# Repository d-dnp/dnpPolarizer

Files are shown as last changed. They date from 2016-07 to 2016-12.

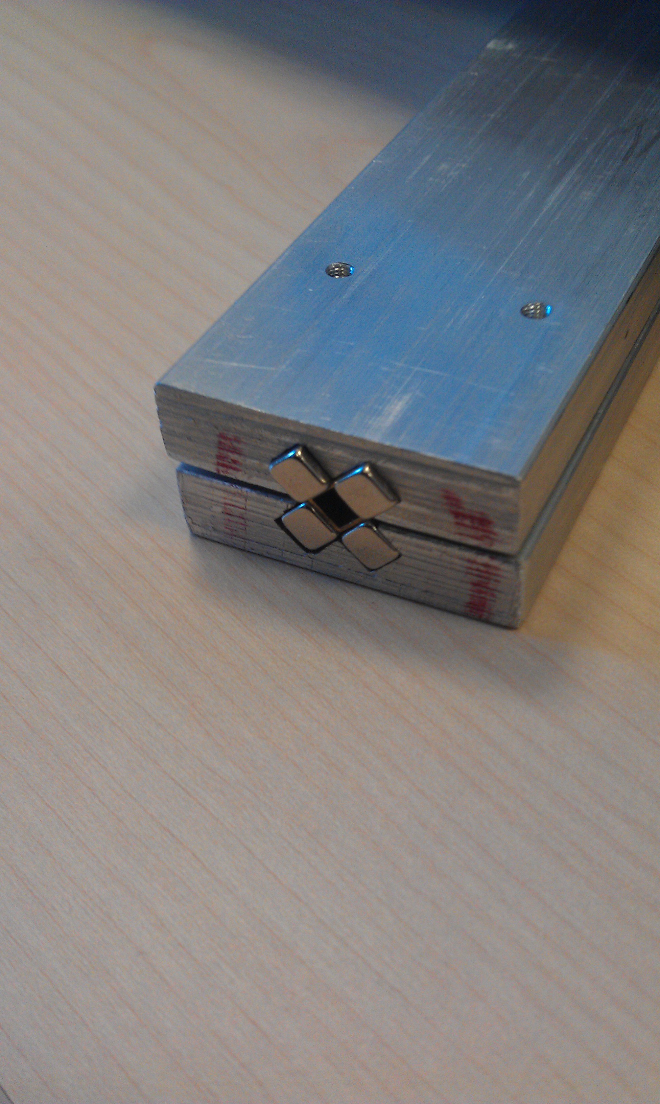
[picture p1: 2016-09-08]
magneticTunnel/Photos/IMAG0099.jpg

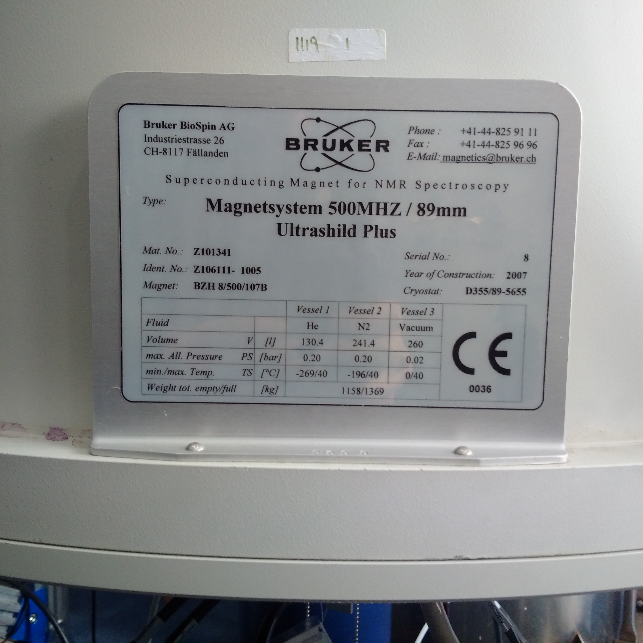
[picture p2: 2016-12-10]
magnet500/magnetInfoPlate500.jpg

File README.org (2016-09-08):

#+TITLE: Dissolution-DNP Polarizer at Southampton University

* Project description
Dissolution-Dynamic Nuclear Polarization (d-DNP) is a technique to enhance the nuclear magnetic reosonance (NMR) signal of small molecules / metabolites by several orders of magnitude. 

Clinical and pre-clinical systems are available commercially, but are costly and cannot provide the felixibility to implement new experimental procedures.

This repository contains the design of the dissolution-DNP system at Southampton University. We hope that it will become a valuable ressource for people working in the field and would be grateful for external contributions / modifications.

Using Trityl and pyruvic acid, a polarization level of 18 % was achieved.

Using TEMPOL and H2O/d-glycerol, a polarization level of 12 % was achieved on sodium acetate.

* The setup at Southampton

The system operates at 6.7 Tesla and uses an Oxford Instruments Spectrostat flow cryostat and a roots pump.

The key components that we are using are as follows: 
| Component                 | Manufacturer       | Approximate Price (EURO)            |
|---------------------------+--------------------+-------------------------------------|
| 6.7 Tesla SWB Magnet      | Bruker             | 60 k (used WB magnets are suitable) |
| Spectrostat Flow Cryostat | Oxford Instruments | 20 k                                |
| Roots Pump, RUVAC WAU251  | Oerlikon           | 20 k                                |
| 188 GHz Microwave Source  | ELVA               | 20 k                                |
| Mini NMR Spectrometer     | Magritek           | 20 k                                |

The use of the Spectrostat Flow cryostat currently limits the temperature to above 2.1 K in continuous mode and 1.8 K in single-shot mode (hold-time approximately 45 mins). 

Options for cryostats with lower base temperature are currently being explored.

** Custom-built components

In addition to these componets, we have designed and built various pieces of instrumentation, listed below. We will shortly add a README file to each of the corresponding folders to provide further information. The mechanical design was performed in SolidWorks. The control electronics rely on the Arduino platform, for which custom printed-circuit board (PCB) extensions, referred to as shields, have been designed in Eagle. The radio-frequency design has been simulated in Python. The project is documented using Emacs org-mode. 

*** DNP insert and CryoShield
The dnp insert allows to irradiate the sample with microwaves at low temperatures down to 1.6K and measure its polarization by NMR. It also hosts a set of Allen-Bradley resistors attached to a custom-built controller/shield. This shield applies 5V pulses to the resistors and measures their resistance as function of time immediately after the pulse. Currently our insert is equipped with coils for 13C and 1H. The coils are roughly tuned and matched with ATC700B chip capacitors, fine tuning is done at room temperatures using an L-Network of Jennings capacitors 1.5 - 45 pF, and optionally coaxial line stretchers (trombone lines) by Microlab.

*** Dissolution Wand and Controller
The controller for the dissolution wand comprises a 220 V to 110 V transformer, whose output can be connected to a mineral barrel heater on the dissolution wand. It also hosts a custom shield that measures the temperature and pressure within the dissolution wand via simple voltage dividers. Finally the controller hosts a relay board to control the various (pilot) valves in the system, including those that drive the dissolution. 

*** Magnetic Tunnel
Following dissolution the solute is flushed to our 500 MHz liquid-state NMR magnet via a magnetic tunnel to reduce low-field relaxation. 

*** Injector
An injector has been designed to fit into our 500 MHz magnet. 

*** Arbitrary Waveform Generator
An arbitrary waveform generator providing an output of up to 24 V has been designed to allow sweeps of the microwave source. We are not using it routinely at the moment, though it is fully functional. 
This device is based on an Arduino Due.

* Procedures
** Sample preparation
More detailed procedures will be in the sample preparation folder.

** Probe tuning
We use an Agilent FieldFox Network Analyser to tune and match our probes. More details will be published soon.

* Acknowledgement
We would like to thank Sami Jannin, Jonas Milani, Jan Hendrik Ardenkjaer-Larsen, Arnaud Comment and Jacques van der Klink for discussions and advice.

* License
#+BEGIN_HTML
<a rel="license" href="http://creativecommons.org/licenses/by-sa/3.0/"><img alt="Creative Commons License" style="border-width:0" src="https://i.creativecommons.org/l/by-sa/3.0/88x31.png" /></a><br />This work is licensed under a <a rel="license" href="http://creativecommons.org/licenses/by-sa/3.0/">Creative Commons Attribution-ShareAlike 3.0 Unported License</a>.
#+END_HTML

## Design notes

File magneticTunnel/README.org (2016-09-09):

* Magnetic Tunnel

** Why 
 
Dissolution-dynamic nuclear polarization (D-DNP) experiments require the use of radical which, when the sample is shuttle through a region of low magnetic field a detection magnet, are efficient in driving longitudinal relaxation of the hyperpolarized substance of interest. A magnetic tunnel has therefor been constructed to provide a high magnetic field region between polarizer and detection magnet to minimise the effect of longitudinal relaxation from dissolved radicals.

** Specs 

Permanent magnets are 5 mm x 5 mm x 50 mm in size and were magnetised to 1x10^6 Am^2 through the short axis. A Haibach array was constructed by arranging permanent magnets in a square with alternating polarity as to augment the magnetic field in the centre of the array creating a magnetic field strength of 0.74 T along the majority of the magnetic tunnels is 2.1 m length. Two magnets, from opposite faces, are removed at each end of the tunnel to avoid flipping the direction of the location magnetic field and ensure a smooth, adiabatic transition from polarizer to magnetic tunnel to detection magnet.

** Results

The magnetic tunnel is predicted to save ~14% spin polarization throughout the dissolution process. Enhancement figures for carbon-13 in sodium acetate without the magnetic tunnel is ~1,500 and with the magnetic tunnel is ~3,900.

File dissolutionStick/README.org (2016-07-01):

#+Title: Dissolution Stick + Box Documentation
This document contains documentation on the wiring / part nos. for the dissolution stick and its controller box.

The controller also drives the pilot valves via 24V lines. A relay module is driven by the Arduino's digital outputs and connects the 24V output of the power supply to the various pins of a DB25 connector on the front panel. 
* Content

** Dissolution Stick
*** Parts
| Part                           |   Order Code | Company  |
|--------------------------------+--------------+----------+
| Pressure Transducer            |     457-3170 | RS       |
| Pt-100                         |     237-1607 | RS       |
| LED green                      |     234-9458 | RS       |
| LED red                        |     234-9420 | RS       |
| Push button with LED           |     729-5429 | RS       |
| Aluminium plates               |      187-328 | RS       |
| M3 Hex Screws                  |     660-4636 | RS       |
| Fischer Connector on Cable     |     726-3337 | RS       |
| Fischer Connector Sleeve       |     1031.855 | RS       |
| Cable: Farnell                 |     119-0173 | Farnelll |
| Manual Valve                   |      SS-4P4T | Swagelok |
| Activated Valve                | 6LVV-DPS6M-C | Swagelok |
| 1/8" Replacement Front Ferrule |      A-203-1 | Swagelok |
| 1/8" Replacement Back Ferrule  |      A-204-1 | Swagelok |
| 1/8" Nylon Nut                 |     NY-202-1 | Swagelok |
| Union cross                    |              | Swagelok |
| Port Connector                 |              | Swagelok |

*** Wiring / Info

** Dissolution Box Controller
*** Dissolution Control
**** Parts
| Part                        | Order Code | Company            |
|-----------------------------+------------+--------------------|
| Rack case 3U                |   665-7637 | RS                 |
| Rack case vented cover      |   665-7652 | RS                 |
| TXL Universal Power Supply  |   418-2308 | RS                 |
| Power switch, fused 4A      |   456-0988 | RS                 |
| Arduino Mega                |            |                    |
| Arduino Ethernet            |   769-7415 | RS                 |
| (Mounting Plate)            |   349-7895 |                    |
|                             |            |                    |
| RJ45 Connector              |   706-0194 | RS                 |
| 5V Solid State Relay module |            | SainSmart / Amazon |
| Transformer Toroidal        |   223-8128 | RS                 |
**** Rack Parts
| Castors for universal rack |   433-7299 |   62.25 |
| 6 way power block          |   686-6165 |  34.704 |
|----------------------------+------------+---------|

**** Wiring / Info
Use C-u <TAB> to expand content
| Colour | Terminal 1         | Terminal 2            | Pin No. on Fischer Connector |
|        |                    |                       |   <5> |
|--------+--------------------+-----------------------+-------|
| Blue   | GND                | GND                   |     1 |
| Green  | 110V AC            | Mineral band heater   |     2 |
| Red    | 110V AC            | Mineral band heater   |     3 |
| Grey   | to GND via A2,100R | Pressure Transducer - |     4 |
| Yellow | EARTH              | EARTH                 |     5 |
| White  | +24V               | Pressure Transducer + |     6 |
| Black  | EARTH              | EARTH                 |     7 |
| Brown  | to 5V via A1,470R  | PT100                 |     8 |
| Violet | to 5V via A0,2K2   | Push button           |     9 |
| Orange | to PIN 10 via 470R | Push button LED       |    10 |
| Rose   | to PIN 11 via 470R | Red LED               |    11 |
| Cyan   | to PIN 12 via 470R | Green LED             |    12 |
| -      | PIN 13             | TTL In, 10K to GND    |       |
| -      | PIN A4             | TTL OUTB              |       |
| -      | PIN A5             | TTL OUTA              |       |

*** Valve Control
**** Parts 
| Part                        | Order Code | Company            |
|-----------------------------+------------+--------------------|
| Sain Smart 5V Relais Module |            | SainSmart / Amazon |
|                             |            |                    |
**** Wiring / Info

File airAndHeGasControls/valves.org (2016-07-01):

* Swagelok actuators
http://www.swagelok.com/downloads/WebCatalogs/EN/MS-02-343.pdf

* Swagelok pneumatically actuated 2 way ball-valve
[[http://www.swagelok.com/search/find_products_home.aspx?part=SS-42GS4-31C#][SS-42GS4-31C]]
243.65 GBP

* Adapter Actuator to 6 mm tubing: RS 536-2606 

* SMC Manifold
** Manifold
http://uk.rs-online.com/web/p/products/762-2036/?origin=PSF_428500|QVBasket%20Summary-LL
222.28 GBP
762-2036
SMC 
SS5Y3-10F1-12B-C6

** Blanking plate
http://uk.rs-online.com/web/p/blanking-plates-for-pneumatic-control-valves/7622095/?origin=PSF_428499|acc
5.14 GBP
762-2095

* SMC Valve
SY3A00-5U1
http://uk.rs-online.com/web/p/pneumatic-solenoid-pilot-operated-control-valves/7622076/
70.83 GBP
762
* Silencer
http://uk.rs-online.com/web/p/pneumatic-silencer-exhaust-restrictor-function-fittings/7622082/
3.43 GBP
762-2082

* 6 mm feed-through
Bulkhead Union 6mm
http://uk.rs-online.com/web/p/pneumatic-bulkhead-tube-to-tube-adaptors/7714936/
4.27 GBP (5 MOQ)
SMC 
KQ2E06-00A

* MOSFET DRIVER 24V
ZXGD3003E6TA, MOSFET Power Driver 5A, Non-Inverting, Maximum of 40V, 6-Pin SOT-23
http://uk.rs-online.com/web/p/mosfet-power-drivers/7122839/
0.189 GBP (50 OQ)

* 25 pin d-sub pcb
http://uk.rs-online.com/web/p/pcb-d-sub-connectors/7183474/

* Feed through for dissolution stick
** Plug (max cable diameter 6.7mm, 0.79mm)
http://uk.rs-online.com/web/p/industrial-automation-circular-connectors/7263324/
PLUG, IP68, PUSH-PULL, 7WAY
33.30 GBP

** Receptable
http://uk.rs-online.com/web/p/industrial-automation-circular-connectors/7263390/?origin=PSF_435588|acc
726-3390
38.58 GBP

* Cable
http://uk.rs-online.com/web/p/cy-cable/4451682/
445-1682
118.02

* Drill/Driver
http://uk.rs-online.com/web/p/cordless-drills-drill-drivers/7525424/
18V XR Li-Ion Compact Drill Driver
215 GBP

* SETUP
  PinOut: [[./SY3000-5000_B_EU-1.pdf::36][Manual page 57]]
  In any case common is pin 13pn
  Pin 1 is the row with more pins, on the side opposite to the
  ports. Then it is clockwise. 

  Next check, if the valve has polarity. Our valve is SY3A00-5U1. U is
  unpolar, so this should be fine. So we have
| Station | Pin | Farbe  |
|---------+-----+--------|
|       1 |   1 | weiss  |
|       2 |  14 | grau   |
|       3 |   2 | lila   |
|       4 |  15 | blau   |
|       5 |   3 | gruen  |
|       6 |  16 | gelb   |
|       7 |   4 | orange |
|       8 |  17 | rot    |
|       9 |   5 |        |
|      10 |  18 |        |
|      11 |   6 |        |
|      12 |  19 |        |

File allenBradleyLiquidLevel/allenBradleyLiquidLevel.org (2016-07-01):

* Configuration.

We use three AB sensors with 100 Ohm resistance at room temperature. They are wired with a 0.2  mm diameter copper cable.

The pin numbering is as follows (the first 4 pins drive current through the resistors.

| Pin | What                           | Color in Cable Assembly |
|-----+--------------------------------+-------------------------|
|   1 | Top AB high side               |                         |
|   2 | Top AB low / Centre AB high    |                         |
|   3 | Centre AB low / Bottom AB high |                         |
|   4 | Bottm AB low                   |                         |
|   5 | AD Top + (parallel to wire 1)  |                         |
|   6 | AD TOP -                       |                         |
|   7 | AD centre +                    |                         |
|   8 | AD centre -                    | red-black               |
|   9 | AD bottom +                    | green-black             |
|  10 | AD bottom -                    | orange-black            |
|  12 | NC                             | blue-black              |
|  14 | Cernox current +               |                         |
|  15 | Cernox current -               |                         |
|  16 | Cernox AD+                     |                         |
|  17 | Cernox AD-                     |                         |

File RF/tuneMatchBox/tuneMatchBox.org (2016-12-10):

* Materials
** Jennings Capacitors
2 x CHV1N-45-0105, 1.5 - 4.5 pF
[[./datasheets/45-260pF-Variable-and-Fix-Vacuum.pdf]]

*** Thread at Shaft: 3/8 32 UNEF
Order code for nut at Farnell: 1202035 

*** Thread at Top: 
1/4 28 UNF Tap: RS: 241-5117
Also fits 1/4 28 fitting for PTFE tubing

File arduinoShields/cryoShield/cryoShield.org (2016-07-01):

This document contains info regarding the wiring of the cryoShield as defined in the eagle [[./cryoShield.brd][file]].

The documentation of the corresponding breakout box can be found here [[/Users/benno/Dropbox/RESEARCH/newPolarizer/cryostats/breakoutBoxOle/breakoutBoxOle.org][here]]

ADG3331 selects the driving potential / current source. 
ADG3332 wires the return path.

See the [[./ADG333A.pdf][manual]].

For Logic 1 Input, Switches switch to the A output

The CS for the AD 7794 was pin 10.

Note that this sketch requires Arduino Pin 4 high to connect the drive current to PIN 1. At the same time Arduino Pin 4 is the Chip Select for the SD functionality.

* BOM 
| Part            | RS Order Code | Quantity |
|-----------------+---------------+----------|
| ADP3303ARZ-3.3  |      697-7713 |        1 |
| Cap 0.1 uF 0805 |      264-4416 |        5 |
| Cap 10 uF 1206  |      464-9069 |        1 |
| Res 220k 0805   |      804-6625 |        1 |
| USB B to USB A  |      815-8466 |        1 |
| AD7794CRUZ      |      709-6676 |        1 |
|                 |               |          |

* Pins
| Arduino Pin | Functionality | Secondary Device | HIGH Connect to | Low Connect to  |
|-------------+---------------+------------------+-----------------+-----------------|
|           0 | free          |                  |                 |                 |
|           1 | free          |                  |                 |                 |
|           2 | IN11          | ADG3331          | +5V             | AD7794 I1       |
|           3 | IN12          | ADG3331          | ADG3331 D3      | ADG3331 D4      |
|           4 | IN13, CS SD   | ADG3331          | Pin 1           | Pin 2           |
|           5 | IN14          | ADG3331          | --              | Pin 3           |
|           6 | IN21          | ADG3332          | 470 Ohm to GND  | GND             |
|           7 | IN22          | ADG3332          | ADG332 D3 to D1 | ADG332 D4 to D1 |
|           8 | IN23          | ADG3332          | Pin 2           | Pin 3           |
|           9 | IN24          | ADG3332          | --              | Pin 4           |
|          10 | CS ETHERNET   |                  |                 |                 |

* Pin Configurations Drive Path
| 2 | 3 | 4 | 5 | Function              |
|---+---+---+---+-----------------------|
| 0 | 0 | 0 | 0 | Connect I1 to Pin 3   |
| 1 | 0 | 0 | 0 | Connect +5V to Pin 3  |
| 1 | 1 | 0 | 0 | Connect +5V to Pin 2  |
| 1 | 1 | 1 | 0 | Connnect +5V to Pin 1 |

* Pin Configuration Return Path
| 6 | 7 | 8 | 9 | Function              |
|---+---+---+---+-----------------------|
| 0 | 0 | 0 | 0 | D1 to GND             |
| 1 | 0 | 0 | 0 | D1 to 470 Ohm to GND  |
| 0 | 0 | 0 | 0 | D4 to D1, Pin 4 to D1 |
| 0 | 1 | 0 | 0 | D3 to D1, Pin 3 to D3 |
| 0 | 1 | 1 | 0 | D3 to D1, Pin 2 to D1 | 

* Probing conditions
Hence for probing the first, second and third resistor with I1, the following pin configurations apply.

Note, that if you want to chase +5V to drive, just set Pin 2 HIGH

The return path connects straight to GND. If you want to connect via 470 Ohm to GND, just set Pin 6 HIGH.

Pin 5 is always low, it connects to Pin 3 and there is no 4th drive pin.
Likewise, Pin 9 is always low, it connects the return path to Pin 4. 

| 2 | 3 | 4 | 5 | 6 | 7 | 8 | 9 | Functionality                             |
|---+---+---+---+---+---+---+---+-------------------------------------------|
| 0 | 1 | 1 | 0 | 0 | 1 | 1 | 0 | Connect I1 to Pin 1, Return Path to Pin 2 |
| 0 | 1 | 0 | 0 | 0 | 1 | 0 | 0 | Connect I1 to Pin 2, Return Path to Pin 3 |
| 0 | 0 | 0 | 0 | 0 | 0 | 0 | 0 | Connect I1 to Pin 3, Return Path to Pin 4 |

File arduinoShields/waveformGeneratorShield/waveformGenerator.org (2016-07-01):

* Description
A waveform generator to sweep microwave frequencies.

It is build around the Arduino Due, DAC0 is used to set the offset,  and DAC1 is used to generate the periodic waveform.

A summing OP amp (AD823, supplied with +/-15 V) is used to generate - (3*V_DAC0 + DAC1). 
The signal is then inverted (AD823).
Then it is fed into a gain = 2 non-inverting Amplifier (again AD823, but powered with +24V / GND. 

At last the signal is filtered by a third order  Butterworth filter with a cutoff frequency of 100 kHz.

* Parts
| Description                       | Brand           | RS order code |
|-----------------------------------+-----------------+---------------|
| TMP15215C Power supply            | Traco           |       6641474 |
| TMP15124C Power supply            | Traco           |       6641468 |
| TMP15105C Power supply            | Traco           |       6641461 |
|-----------------------------------+-----------------+---------------|
| Interscale M19" Enclosure 2U      | Schroff         |       8104387 |
| Mounting plate                    | Schroff         |       8104425 |
| PCB holder                        | Schroff         |       8104529 |
| LED 12V                           | RS Pro          |       8987683 |
| Ethernet Connector                | TE Connectivity |       7060194 |
| USB Connector                     | Harting         |       7658757 |
| BNC Connector                     | TE Connectivity |       5121174 |
| OR SMA Connector                  | TE Connectivity |      512-0008 |
| Mains connector                   | Bulgin          |      211-0985 |
| Slow blow Fuse                    | Schurter        |       7897801 |
|-----------------------------------+-----------------+---------------|
| AD823                             | Analog Devices  |       5237409 |
| DIL Socket                        | Winslow         |        813115 |
| Terminal Block                    | Phoenix         |       6487863 |
| SMA Connector                     | TE Connectivity |       6163422 |
| 0.1" Header                       |                 |               |
|-----------------------------------+-----------------+---------------|
| 2 x SMA - SMB Cable for Microwave | RF Solutions    |       7043502 |
| SMB - SMB adaptor                 | TE Connectivity |       2955766 |
| Right Angle SMA connector RG58    | RS Pro          |       5463232 |
| Right angle SMB connector         | TE Connectivity |       4205388 |
|                                   |                 |               |

5120008
2110985
7897801
813115
4205366
5463232

* Assembly instructions
Arduino Due mount: Drill holes as per [[file:~/Dropbox/RESEARCH/newPolarizer/arduino/arduinoDrawing.pdf][Drawing]]
(The upper two holes should be used only with insulating supports since they are too close to some pins)

Power supplies: 4 holes 3 - 3.5 mm Diameter on a 46 by 86 mm lattice. 
Supply dimensions are 54 by 96 mm.
* Programming
  [[./Atmel-11057-32-bit-Cortex-M3-Microcontroller-SAM3X-SAM3A_Datasheet.pdf][Datasheet]]
  Range is 0.58 to 2.24 V, see datasheet, p. 1033), according to this [[http://forum.arduino.cc/index.php?topic=154965.0][post]]
  Page 1412 specifies the range as 1/6 ADVREF to 5/6 ADVREF
  But ADVREF is 3.3V as can be seen from this [[./schema.jpg][scheme]] taken from this [[http://forum.arduino.cc/index.php?topic=193643.0][post]]

  Regarding speed and timing accuracy, a Timer is key and check this post
  http://rcarduino.blogspot.co.uk/2012/11/quick-and-dirty-synth-for-arduino-due.html

  So the range is 0.55 to 2.75 V at the DACs outputs.

  The offset (DAC0) is multiplied by 3, and the ramp (DAC0) by one. 
  That signal is then  multiplied by 2, so in total the minimum voltage is
  (* 0.55 4 2) = 4.4 V and the maximum voltage is
  (* 2.75 4 2) = 22 V

  We want to sweep from 12.17 to 13.05V. 
  Since DAC1 is only multiplied by 2, we need to sweep DAC1 by
  (/ (- 13.05 12.17) 2) = 0.44V

  So lets sweep DAC1 from 0.55 to 0.99 V or 20% of its range. 

  This will have an offset of 1.1V, so need to configure DAC0 to give 11.07 V.
  DAC0 is multiplied by 6, so we need to set it to (/ 11.07 6) = 1.845 V.
  This is 1.295V above its base value, corresponding to (/ 1.295 2.2) 58.9 % of its output range.

  (* 4095 0.589) = 2412
  (* 4095 0.2)  = 918

* Ethernet Interface
  An Ethernet interface is implemented. The python module to communicate with the waveform generator is [[~/Dropbox/RESEARCH/newPolarizer/software/waveformGenerator.py][here]].

#+BEGIN_SRC python
import waveformGenerator as wG

address = ('10.1.15.232', 5000)

waveGen = wG.waveformGenerator(address)

wG.set("DAC0", 15)
wG.set("DAC1", 32)
#+END_SRC

** Manual control 
In this mode one can set the values of DAC1 and DAC2 seperately.

* Calibration
Calibration is done by measuring the output with a Keithley 2400 source meter.

We obtain excellent linearity

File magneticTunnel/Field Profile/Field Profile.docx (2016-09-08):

11.74T

6.70mT

6.695mT

2.40T

10.0mT

0.74T

Plot of the magnetic field vector along the dissolution trajectory. The entire trajectory is 4.65m. x(m) is the distances along the trajectory and |B0|(T) is the absolute magnetic field values. The Polarizer has an absolute field value of 6.70T at its magnetic field centre. At the “hold position” for dissolution experiments, which is 10cm above the magnetic field centre, the field if 6.695T. This is in a flat region of the magnetic field profile. The magnetic tunnel has a simulated (COMSOL MULTIPHYSICS) magnetic field amplitude of 0.74T. The phase separator is located 27.5cm above the magnetic field centre of the 500 MHz magnet. The field at this region is 2.40T but is located along a sharp magnetic field gradient. The field at the magnetic sweet spot of the 500 MHz magnet is 11.74T. For this plot I have used the “on axis” plots of the magnetic field vector in the bore of each instrument. The “on axis” data was provided by Bruker.

Plots of x against Log|B0| are also included. The gridlines indicate the same locations and magnetic field strengths as before.

Above are plots of the magnetic field amplitude as one enters (left) and leaves (right) the magnetic tunnel. I have assumed a distances of 10cm between the edges of the magnetic tunnel and the top of the bore for each instrument. The magnetic field deviations at 1.81m and 3.66m are due to the “transition region” at the ends of the magnetic tunnel. This avoids a zero-crossing of the magnetic field vector. These transitions are adiabatic.

[Type text][Type text][Type text]

Stuart ElliottV2-Dissolution Magnetic Field Profile2

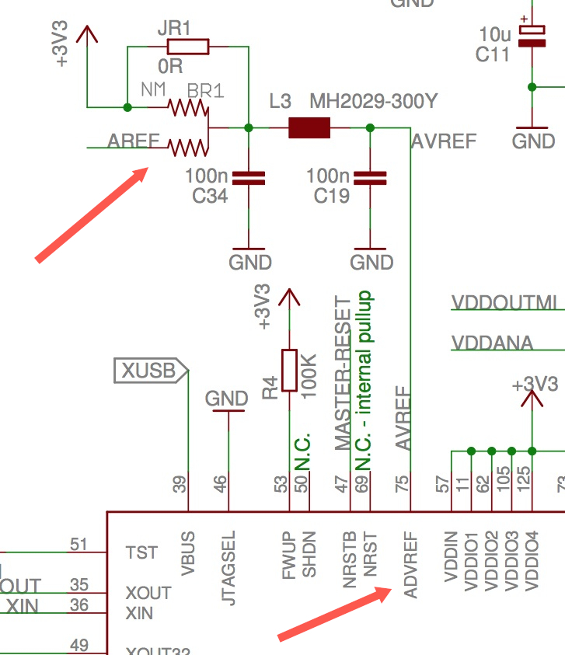
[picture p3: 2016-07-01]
software/firmware/waveformGenerator/schema.jpg

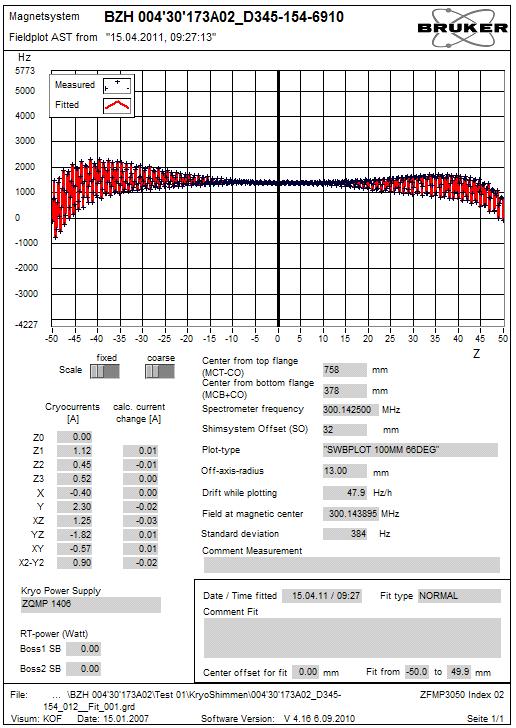
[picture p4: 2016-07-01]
magnet300/fieldMaps/fieldPlotAST.jpeg

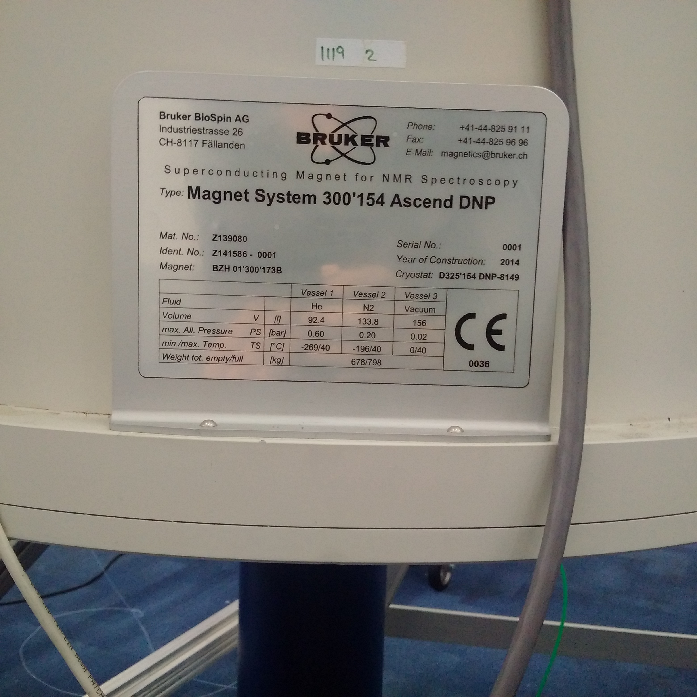
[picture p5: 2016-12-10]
magnet300/magnetInfoPlate300SWB.jpg

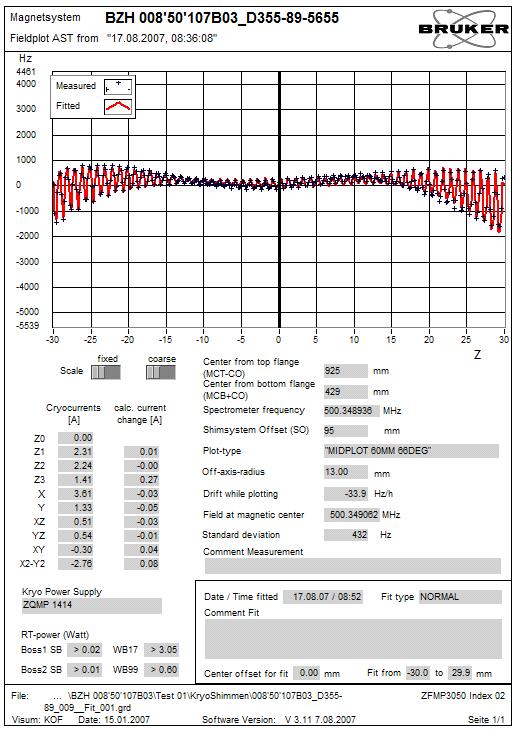
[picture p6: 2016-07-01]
magnet500/fieldMaps/fieldPlotAST.jpeg

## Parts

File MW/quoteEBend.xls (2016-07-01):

 |  |  | RF.COM Ltd
 |  |  | RF House
 |  |  | 109/12a2 Swanston Road
 |  |  | Edinburgh
 |  |  | EH10 7DS
 |  |  | Tel. +44 (0)131 452 8777
 |  |  | Fax. +44(0)131 452 8666
 |  |  | Email. Sales@rfcom.co.uk
 |  |  | Web. www.rfcom.co.uk
To: |  |  | Telephone: |  |  | Date:
 |  |  |  |  |  | 2014-06-12
Benno Meier |  |  | Fax: |  |  | Quote Reference:
 |  |  |  |  |  | RFCSM4132
Southampton University |  |  | E Mail: |  |  | RFCOM Contact:
 |  |  | b.meier@ston.ac.uk |  |  | Sharon McIlhone | Ian Cains
 |  |  | Your Reference: |  |  | Contact Email:
 |  |  | Telephone call |  |  | sharon@rfcom.co.uk
Item | Part Number | Description |  | Quantity | Unit price |  | Delivery
1 |  | WR-05 Waveguide |  | 1 & 2 | £395.00 |  | 6-8 weeks aro
 |  | UG-387/U-M flanges
 |  | Silver plated, painted
2 |  | Delivery per drop |  |  | £15.00
This quotation is valid for a period of 30 days unless otherwise stated. Prices |  |  | Signed: |  |  | Payment Terms:
are quoted in UK£ (Sterling) and include import duty charges. |  |  | Sharon McIlhone
Any order ensuing from this quotation is subject to RF.COM's |  |  | ………………………………………………………… |  |  | Net 30 Days
standard terms and conditions. |  | Prices Exclude VAT
The above prices are based on today's exchange rate taken from the National
Westminster quoted rates. Should this rate vary by 5% or more at the time of
invoice RF Com Ltd reserve the right to adjust the invoice amount accordingly.

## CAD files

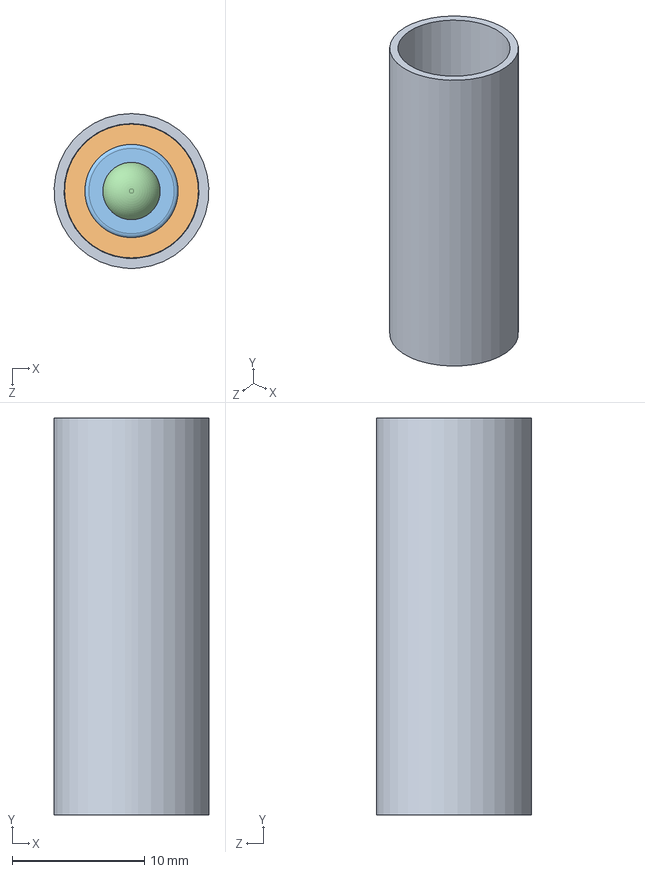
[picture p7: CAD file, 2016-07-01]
dnpInsert/V3/filledSampleTubeAssembly.SLDASM
11.7 x 30.0 x 11.7 mm
sampleTubeBottom_G10
sampleTubeBottomPEEK
sampleCup
sample

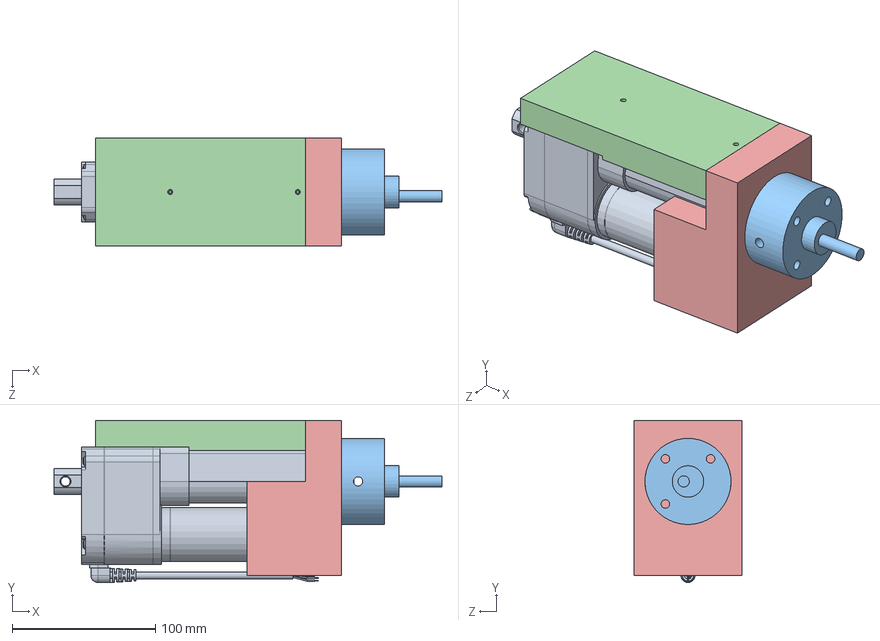
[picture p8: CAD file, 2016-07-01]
injection/linActPlatformAssem.SLDASM
270.5 x 113.0 x 75.0 mm
_CAHB10-050-AA-P-A-b
_CAHB10-050-P-AA-A-r
pistonTopHolder_linAct
linActPlatform1
linActPlatform2

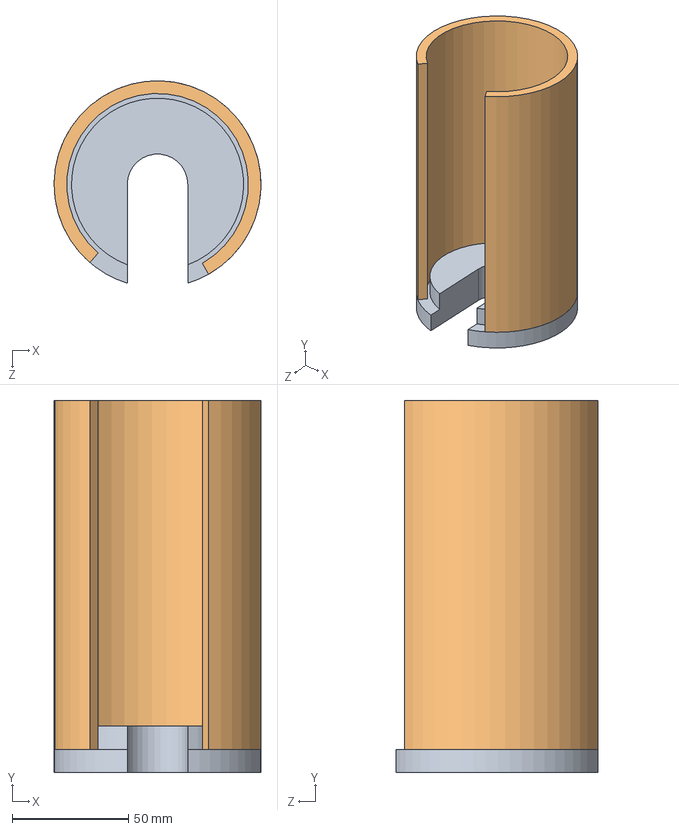
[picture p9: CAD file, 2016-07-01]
dissolutionStick/sampleTubeSupport/sampleTubeSupportAssem.SLDASM
89.0 x 160.0 x 87.1 mm
lid
tube

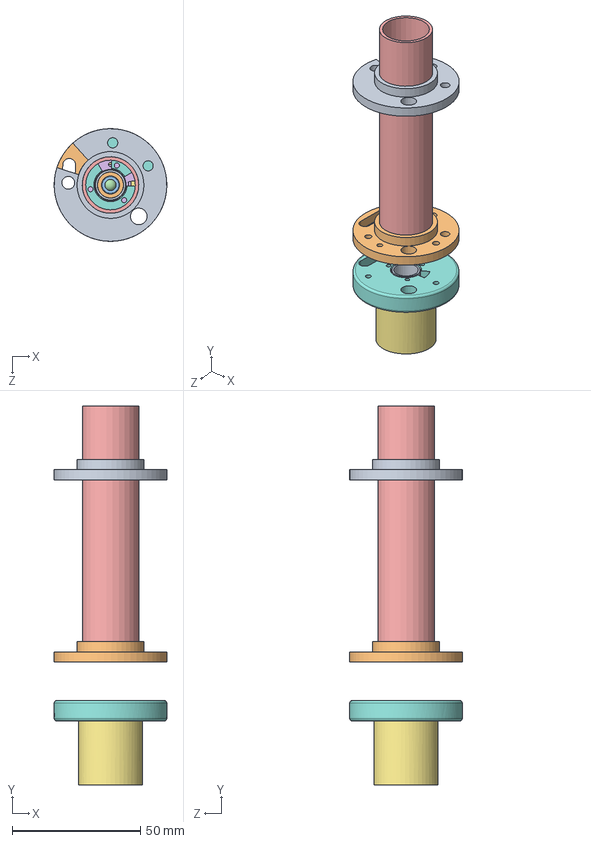
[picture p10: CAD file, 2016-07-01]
dnpInsert/V3/insertAssembly.SLDASM
44.0 x 148.0 x 44.0 mm
sampleTubeBottom_G10
sampleTubeBottomPEEK
sampleCup
sample
insertTubeEnd
coilSupport
cavity
cavityLid
radiationBaffle
sampleTubeBottomFlange

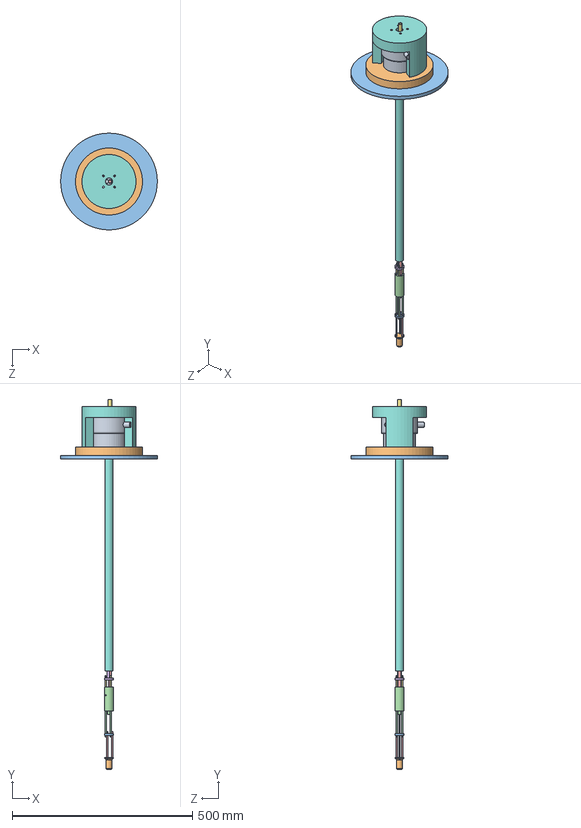
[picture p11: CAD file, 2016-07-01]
injection/injectorPlusMagnet.SLDASM
268.4 x 1027.0 x 268.6 mm
barril
barrilClamp
magnetBore
injector4
piston3
injectorHolder1
bastonT1 x 3
chamberG10tube
center disc x 4
spinner
spinnerHolder
spinnertubes2 x 3
spinnertubes x 3
topHolder
pistonG10tube

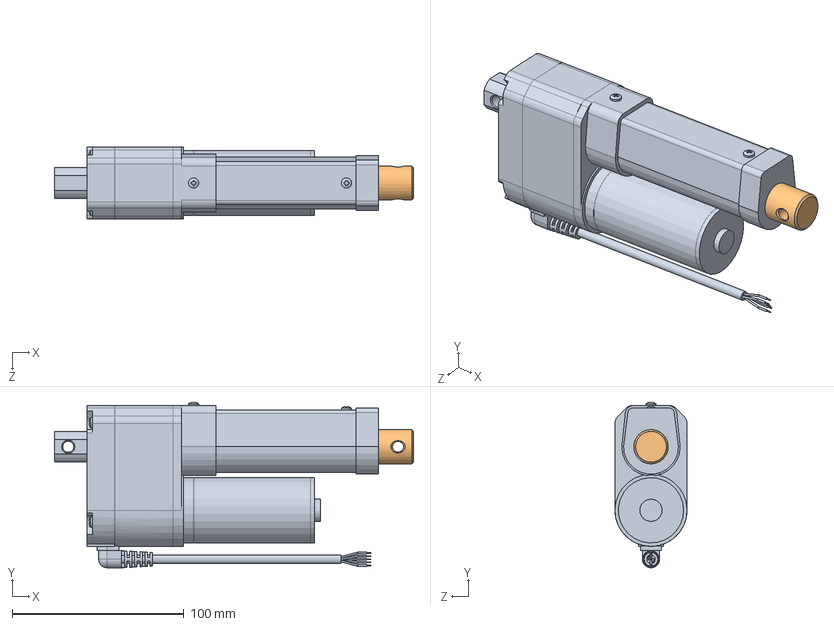
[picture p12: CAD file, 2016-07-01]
injection/CAHB-10-B2A-050-AAAAPA-000.SLDASM
209.0 x 96.4 x 42.0 mm
_CAHB10-050-AA-P-A-b-1
_CAHB10-050-P-AA-A-r-1

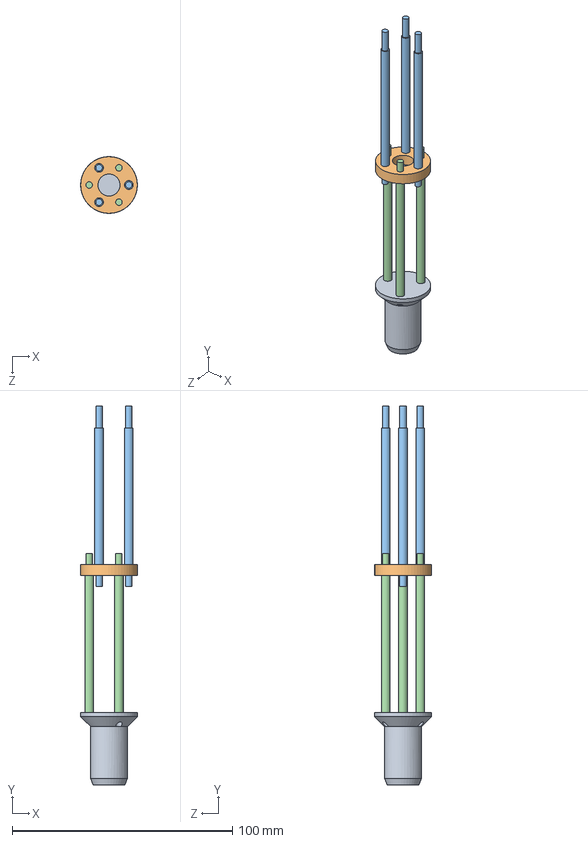
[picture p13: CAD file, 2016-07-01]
injection/spinnerAssem.SLDASM
25.7 x 172.0 x 25.8 mm
spinner
spinnerHolder
spinnertubes2 x 3
spinnertubes x 3

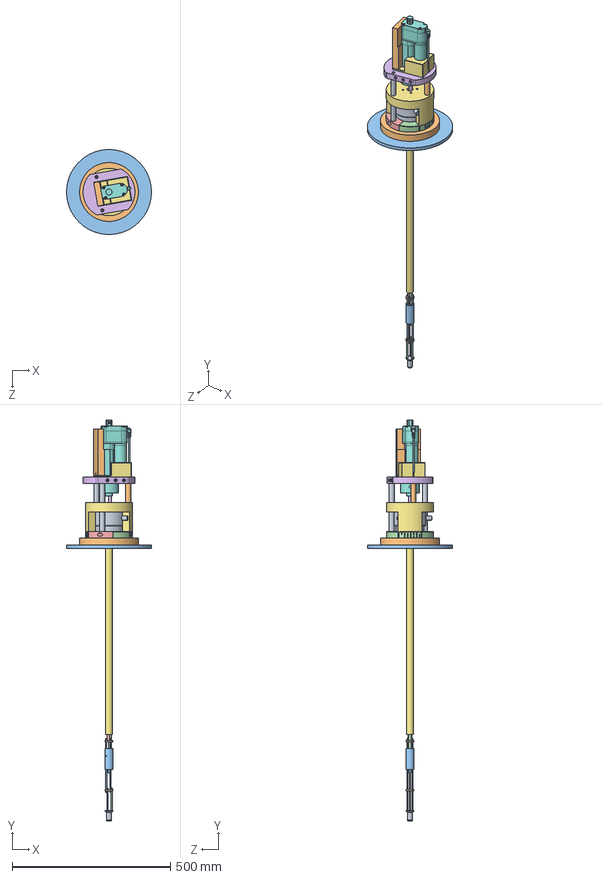
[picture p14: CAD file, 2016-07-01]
injection/injectorFinalAssem.SLDASM
268.4 x 1267.5 x 268.6 mm
barril
barrilClamp
magnetBore
linActPlatform4
linActPlatform3
linActPlatform5
linActPlatform2
_CAHB10-050-AA-P-A-b-1
_CAHB10-050-P-AA-A-r-1
linActPlatform1
injector4
piston3
injectorHolder1
bastonT1 x 3
chamberG10tube
center disc x 4
spinner
spinnerHolder
spinnertubes2 x 3
spinnertubes x 3
topHolder
pistonG10tube
pistonTopHolder_linAct
peekColumn x 2
peekColumn2

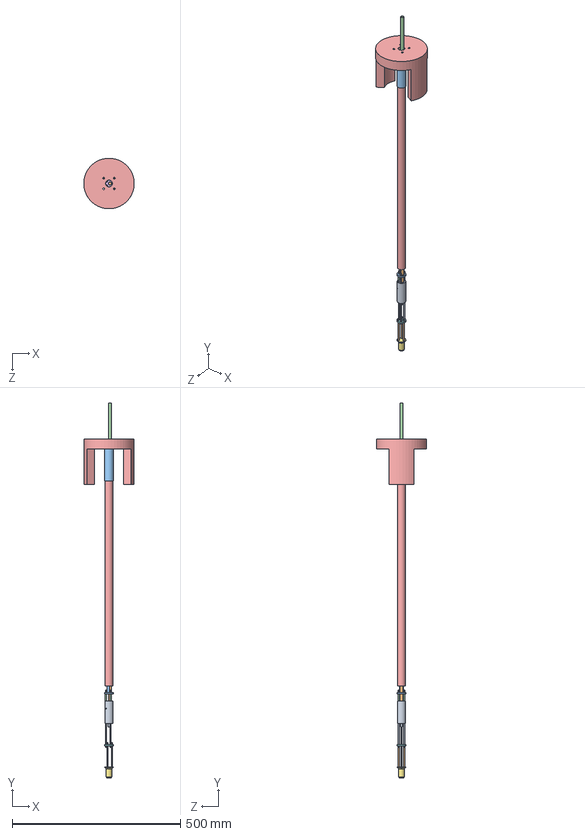
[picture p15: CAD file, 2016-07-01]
injection/injectAssem1.SLDASM
149.9 x 1114.0 x 150.0 mm
injector4
piston3
injectorHolder1
bastonT1 x 3
chamberG10tube
center disc x 4
spinner
spinnerHolder
spinnertubes2 x 3
spinnertubes x 3
topHolder
pistonG10tube

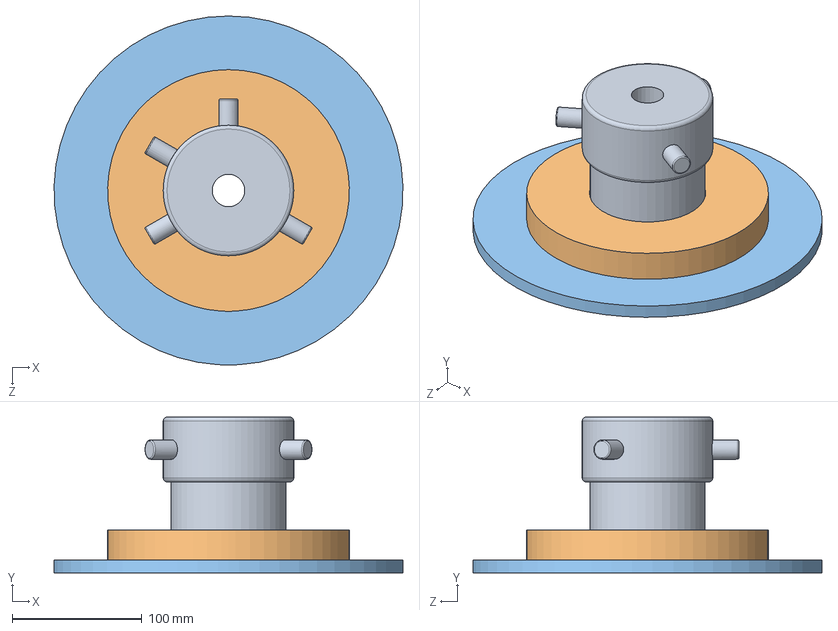
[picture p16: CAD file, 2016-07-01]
injection/magnetPlusBarril.SLDASM
268.4 x 120.0 x 268.6 mm
barril
barrilClamp
magnetBore

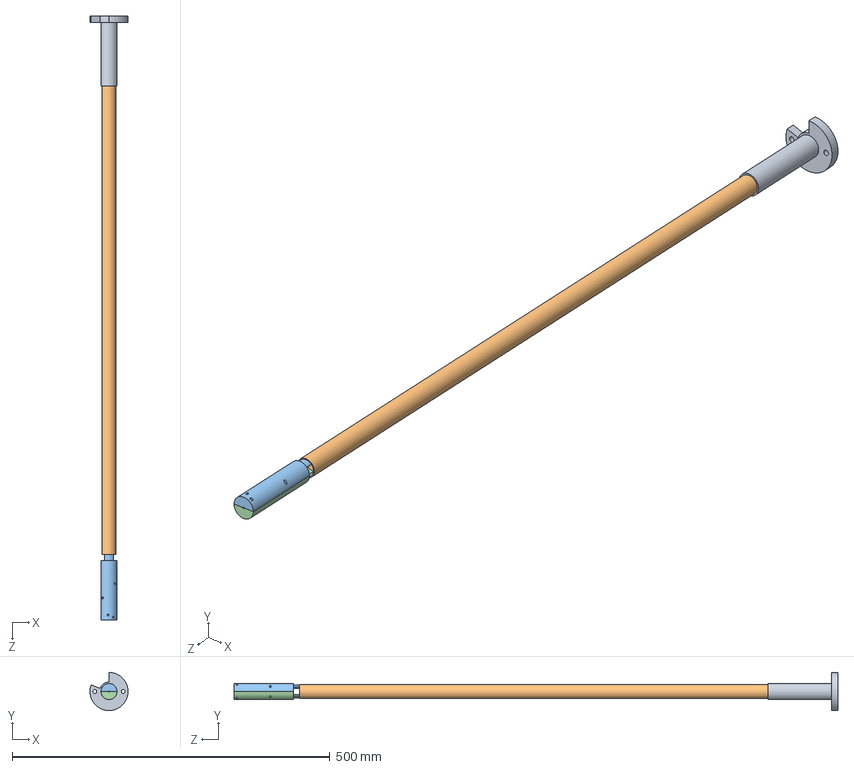
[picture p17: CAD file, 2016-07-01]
injection/injectorAssambly.SLDASM
59.9 x 60.0 x 950.0 mm
topHolder
g10TubeHolder
injector2
injector2Inv

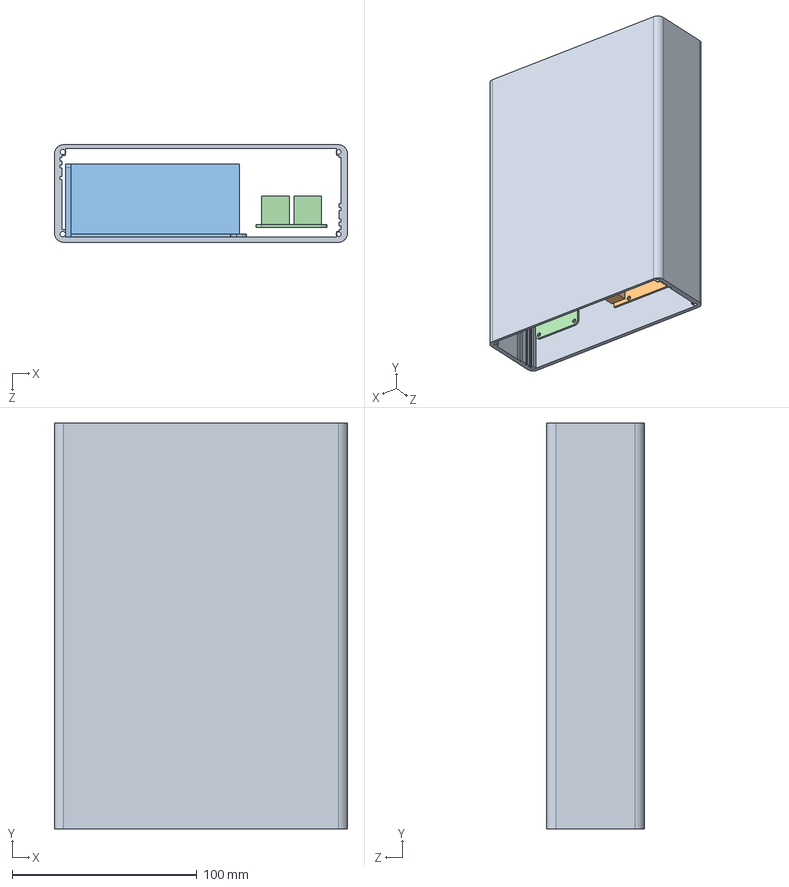
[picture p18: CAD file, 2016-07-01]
injection/controlBox.SLDASM
158.8 x 220.0 x 53.0 mm
arduino
powerSup
relay

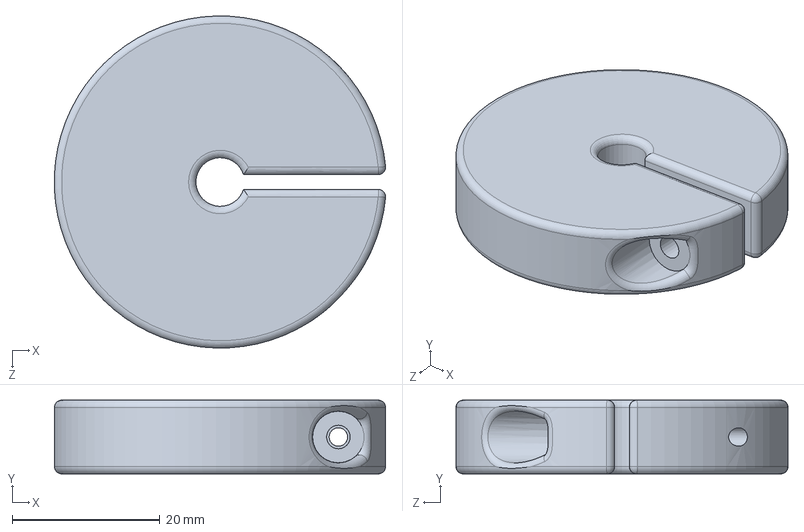
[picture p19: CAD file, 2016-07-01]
cryostats/HallProbeClampOxInst.SLDPRT
44.9 x 10.0 x 45.0 mm

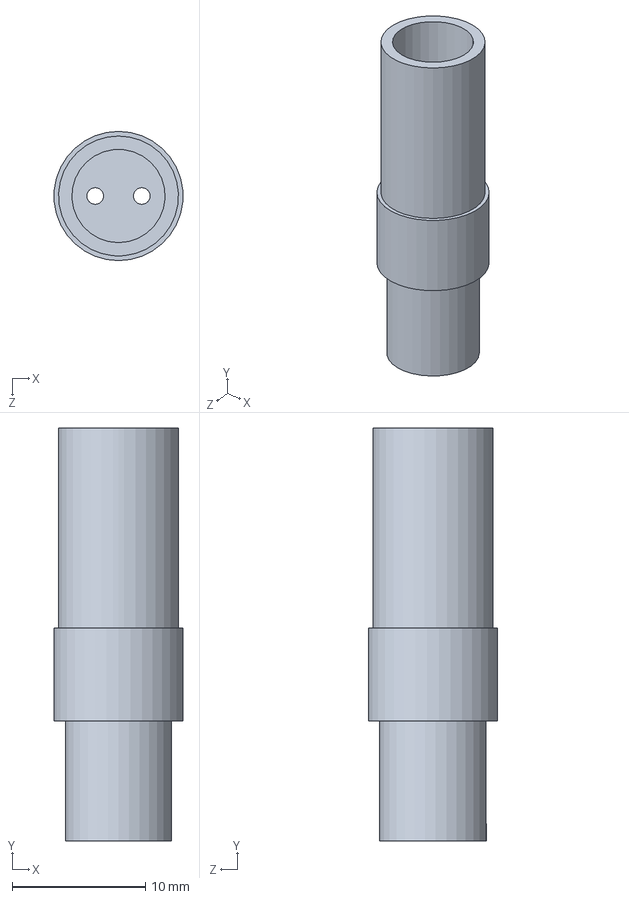
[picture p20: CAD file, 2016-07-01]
dissolutionStick/dissBit/dissBit4.SLDPRT
9.66 x 31.0 x 9.70 mm

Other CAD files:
arduinoDrawing/arduinoDrawing.SLDPRT
dissolutionStick/dissChamberParts/bottomPlasticPlate.SLDPRT
dissolutionStick/plattformAttachment/hook1.SLDPRT
dissolutionStick/sampleTubeSupport/tube.SLDPRT
MW/uwave/uwWindow.stl
MW/waveGuideTaper3over8x0p008wall.SLDDRW
MW/waveGuideTaper3over8x0p008wall.SLDPRT
MW/waveGuideTaper3over8x0p008wall.STL
RF/javierCoilSupport/javierCoilSupport.SLDPRT
RF/javierCoilSupport/javierCoilSupport.STL
RF/tuneMatchBox/drawings/capacitorOuterPart.SLDPRT
arduinoDrawing/arduinoDrawing.SLDDRW
cryostats/HallProbeClampOxInst.STL
cryostats/OxfordCryostatCenteringPiece300.SLDPRT
cryostats/OxfordCryostatCenteringPiece300.STL
cryostats/OxfordCryostatCenteringPiece300_rev1.SLDPRT
dissolutionStick/dissBit/dissBit4.SLDDRW
dissolutionStick/dissChamberParts/bottomPlasticPlate.STL
dissolutionStick/dissChamberParts/handleOne.SLDPRT
dissolutionStick/dissChamberParts/handleTwo.SLDPRT
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

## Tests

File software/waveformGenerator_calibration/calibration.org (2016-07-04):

#+BEGIN_SRC python no-theme-inherit :results ouput :exports both
import numpy as np
print "Hello"
#+END_SRC python

#+RESULTS:

(org-babel-do-load-languages
 'org-babel-load-languages
 '((python . t)))

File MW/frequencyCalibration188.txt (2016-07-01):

0.0000 186604.4000
0.4490 186671.2000
0.8980 186731.4000
1.3469 186788.1000
1.7959 186841.6000
2.2449 186892.8000
2.6939 186941.7000
3.1429 186989.9000
3.5918 187036.5000
4.0408 187082.9000
4.4898 187127.6000
4.9388 187172.3000
5.3878 187216.0000
5.8367 187259.4000
6.2857 187302.2000
6.7347 187344.8000
7.1837 187386.1000
7.6327 187427.9000
8.0816 187468.4000
8.5306 187509.1000
8.9796 187549.8000
9.4286 187589.5000
9.8776 187630.2000
10.3265 187670.2000
10.7755 187709.8000
11.2245 187750.9000
11.6735 187791.3000
12.1224 187831.0000
12.5714 187872.0000
13.0204 187911.4000
13.4694 187953.2000
13.9184 187995.3000
14.3673 188037.6000
14.8163 188082.9000
15.2653 188129.7000
15.7143 188176.8000
16.1633 188226.9000
16.6122 188277.7000
17.0612 188328.9000
17.5102 188381.6000
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

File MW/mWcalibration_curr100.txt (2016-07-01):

0.0000 14078.0000 186604.2000
0.4214 14078.0000 186666.5000
0.8429 14078.0000 186722.9000
1.2643 14072.0000 186775.9000
1.6857 14072.0000 186826.2000
2.1071 14085.0000 186874.1000
2.5286 14072.0000 186920.2000
2.9500 14085.0000 186965.2000
3.3714 14078.0000 187009.4000
3.7929 14085.0000 187052.2000
4.2143 14078.0000 187094.8000
4.6357 14072.0000 187136.9000
5.0571 14085.0000 187178.2000
5.4786 14072.0000 187219.4000
5.9000 14072.0000 187260.4000
6.3214 14078.0000 187300.4000
6.7429 14085.0000 187340.8000
7.1643 14085.0000 187380.8000
7.5857 14085.0000 187419.9000
8.0071 14072.0000 187459.3000
8.4286 14078.0000 187498.5000
8.8500 14078.0000 187536.5000
9.2714 14091.0000 187575.4000
9.6929 14078.0000 187614.0000
10.1143 14078.0000 187651.6000
10.5357 14078.0000 187690.4000
10.9571 14085.0000 187729.0000
11.3786 14085.0000 187767.1000
11.8000 14078.0000 187806.0000
12.2214 14078.0000 187844.8000
12.6429 14078.0000 187882.6000
13.0643 14085.0000 187921.5000
13.4857 14072.0000 187960.9000
13.9071 14072.0000 187999.8000
14.3286 14065.0000 188041.6000
14.7500 14078.0000 188084.2000
15.1714 14085.0000 188127.8000
15.5929 14078.0000 188173.6000
16.0143 14078.0000 188220.5000
16.4357 14085.0000 188267.4000
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

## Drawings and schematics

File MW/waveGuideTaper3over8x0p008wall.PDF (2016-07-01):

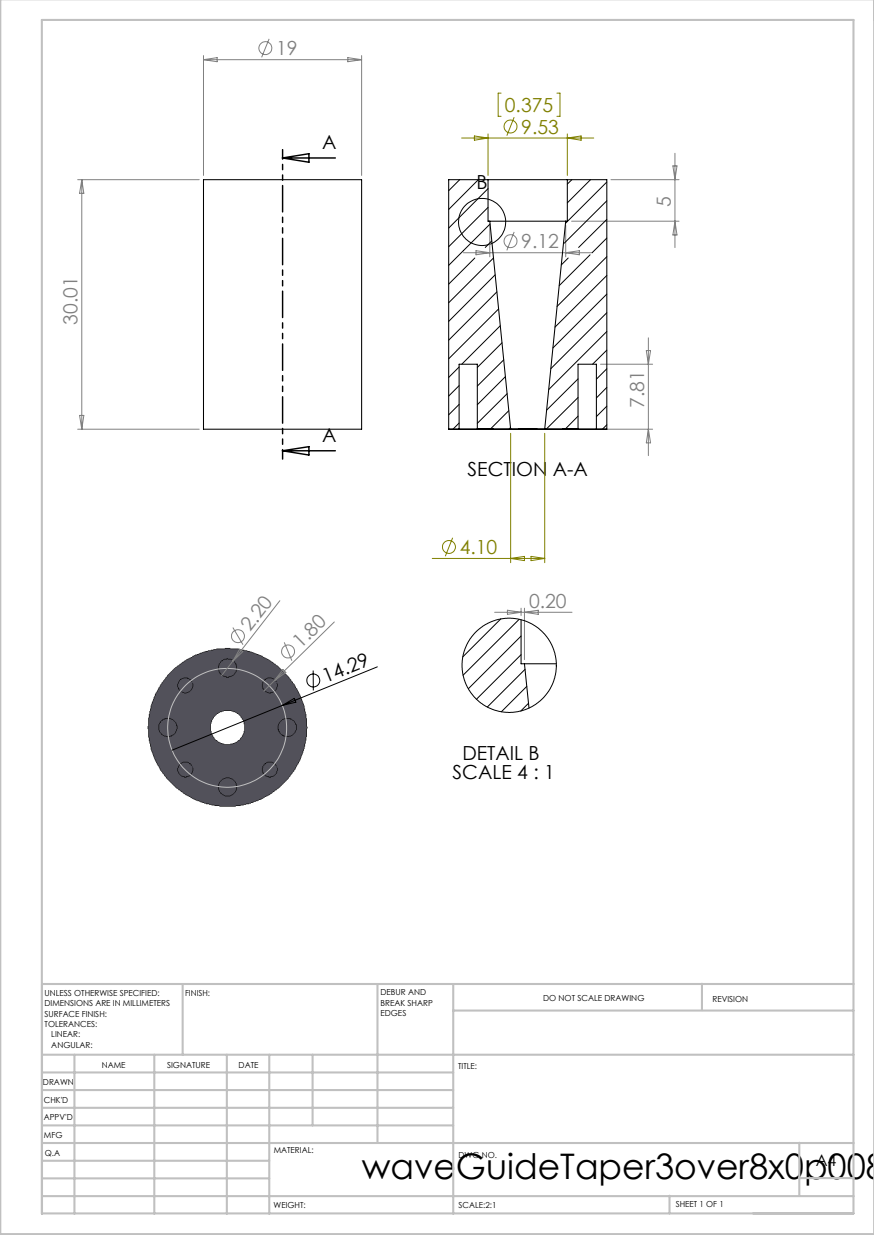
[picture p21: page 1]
SECTION A-A; DETAIL B SCALE 4 : 1; SCALE:2:1; SHEET 1 OF 1; DO NOT SCALE DRAWING; REVISION; DEBUR AND BREAK SHARP; UNLESS OTHERWISE SPECIFIED:; FINISH:

DIMENSIONS ARE IN MILLIMETERS
SURFACE FINISH:
TOLERANCES:
LINEAR:
ANGULAR:

NAME | SIGNATURE | DATE | | | | TITLE:
Q.A | | | | waveGuideTaper3over8x0p008wall WEIGHT: MATERIAL: | DWG NO. | A4

DRAWN
CHK'D
APPV'D
MFG

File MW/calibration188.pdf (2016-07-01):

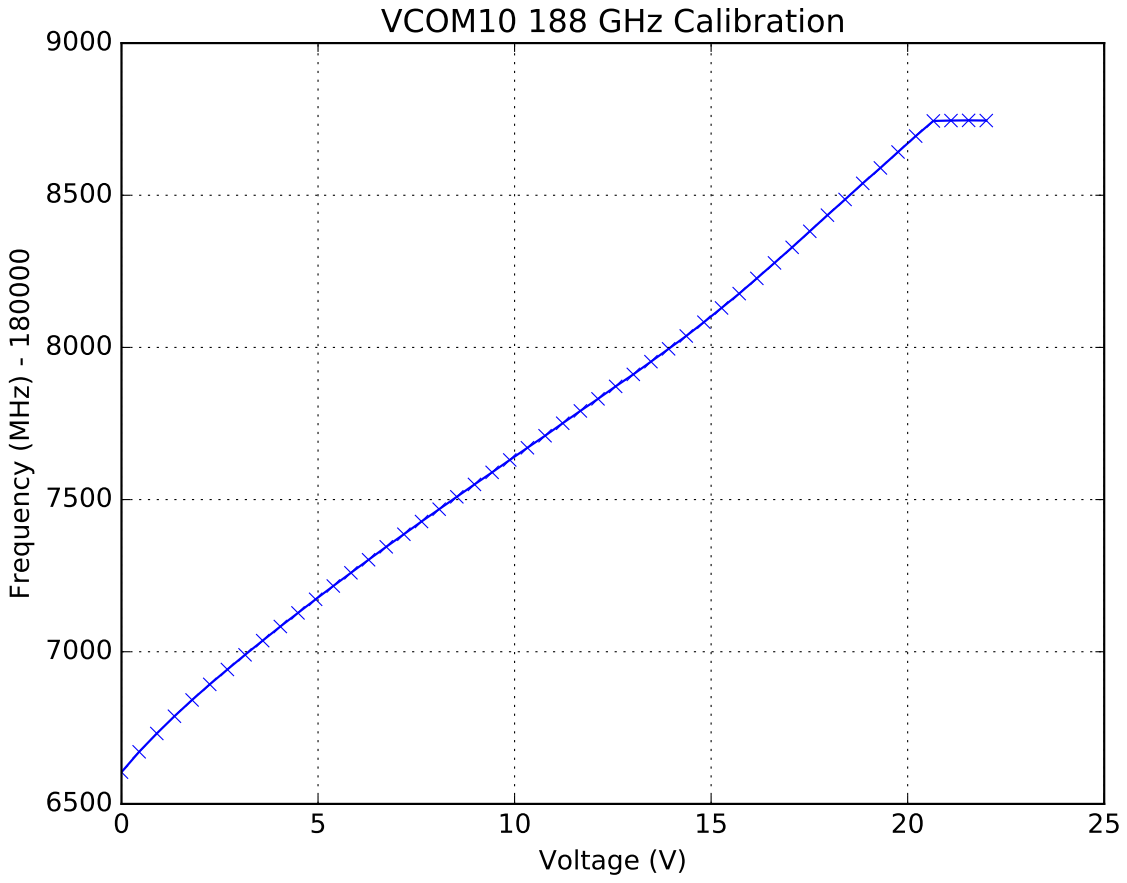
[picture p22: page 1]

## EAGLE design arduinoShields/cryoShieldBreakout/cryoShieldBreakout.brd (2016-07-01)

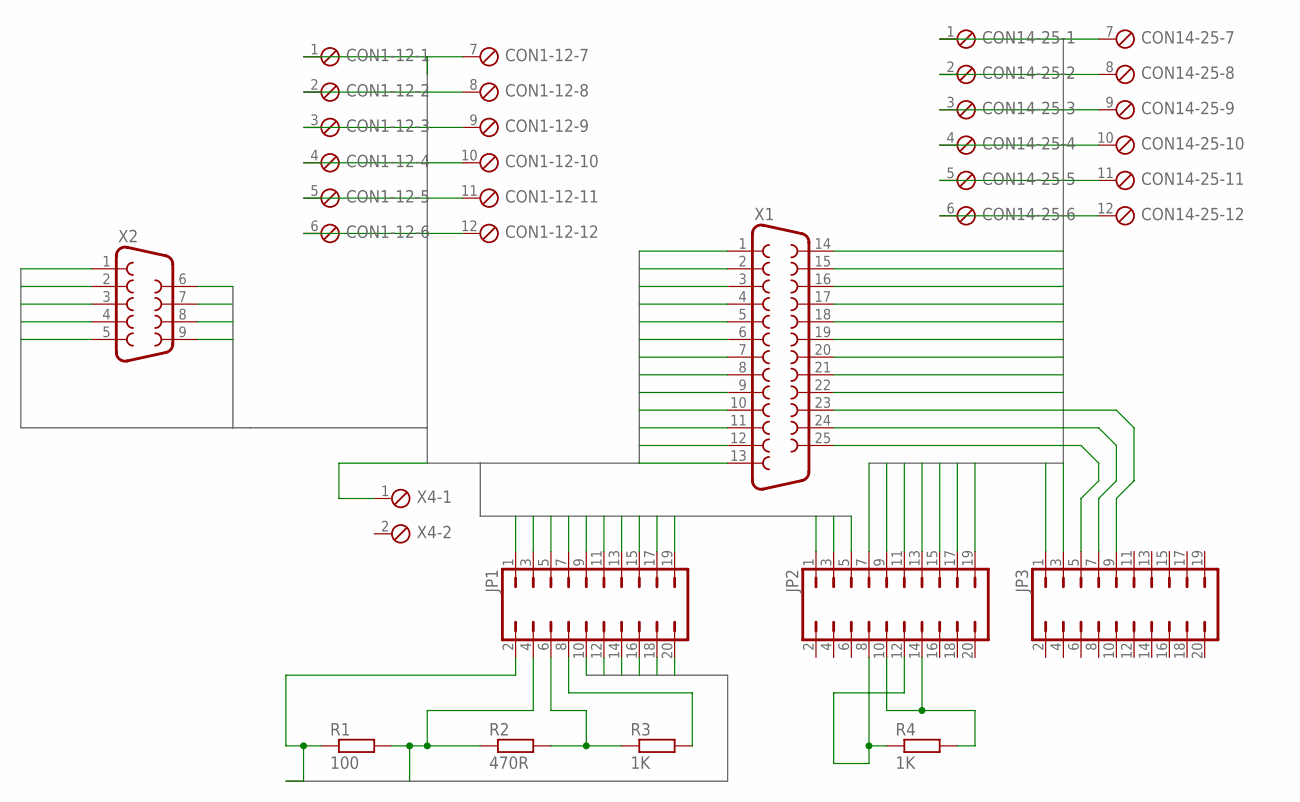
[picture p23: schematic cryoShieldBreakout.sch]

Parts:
CON1-12, CON14-25: MPT12; 12POL254
JP1, JP2, JP3: JP10Q
R1: 100; 0207/10
R2: 470R; 0207/10
R3, R4: 1K; 0207/10
X1: F25H
X2: F09H
X4: MPT2; 2POL254

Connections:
1: CON1-12.1, JP1.1, X1.1, X2.1
2: CON1-12.2, JP1.3, X1.2, X2.2
3: CON1-12.3, JP1.5, X1.3, X2.3
4: CON1-12.4, JP1.7, X1.4, X2.4
5: CON1-12.5, JP1.9, X1.5, X2.5
6: CON1-12.6, JP1.11, X1.6, X2.6
7: CON1-12.7, JP1.13, X1.7, X2.7
8: CON1-12.8, JP1.15, X1.8, X2.8
9: CON1-12.9, JP1.17, X1.9, X2.9
10: CON1-12.10, JP1.19, X1.10
11: CON1-12.11, JP2.1, X1.11
12: CON1-12.12, JP2.3, X1.12
13: JP2.5, X1.13, X4.1
14: CON14-25.1, JP2.7, X1.14
15: CON14-25.2, JP2.9, X1.15
16: CON14-25.3, JP2.11, X1.16
17: CON14-25.4, JP2.13, X1.17
18: CON14-25.5, JP2.15, X1.18
19: CON14-25.6, JP2.17, X1.19
20: CON14-25.7, JP2.19, X1.20
21: CON14-25.8, JP3.1, X1.21
22: CON14-25.9, JP3.3, X1.22
23: CON14-25.10, JP3.5, X1.23
24: CON14-25.11, JP3.7, X1.24
25: CON14-25.12, JP3.9, X1.25
A1+: JP1.2, JP1.10, R1.1
A1-: JP1.4, R1.2, R2.1
A2+: JP1.12, JP1.14
A3+: JP1.16, JP1.18
A3-: JP1.20
unnamed: JP2.8, JP2.12, R4.1
unnamed: JP2.10, JP2.14, R4.2
unnamed: JP1.6, R2.2, R3.1
unnamed: JP1.8, R3.2

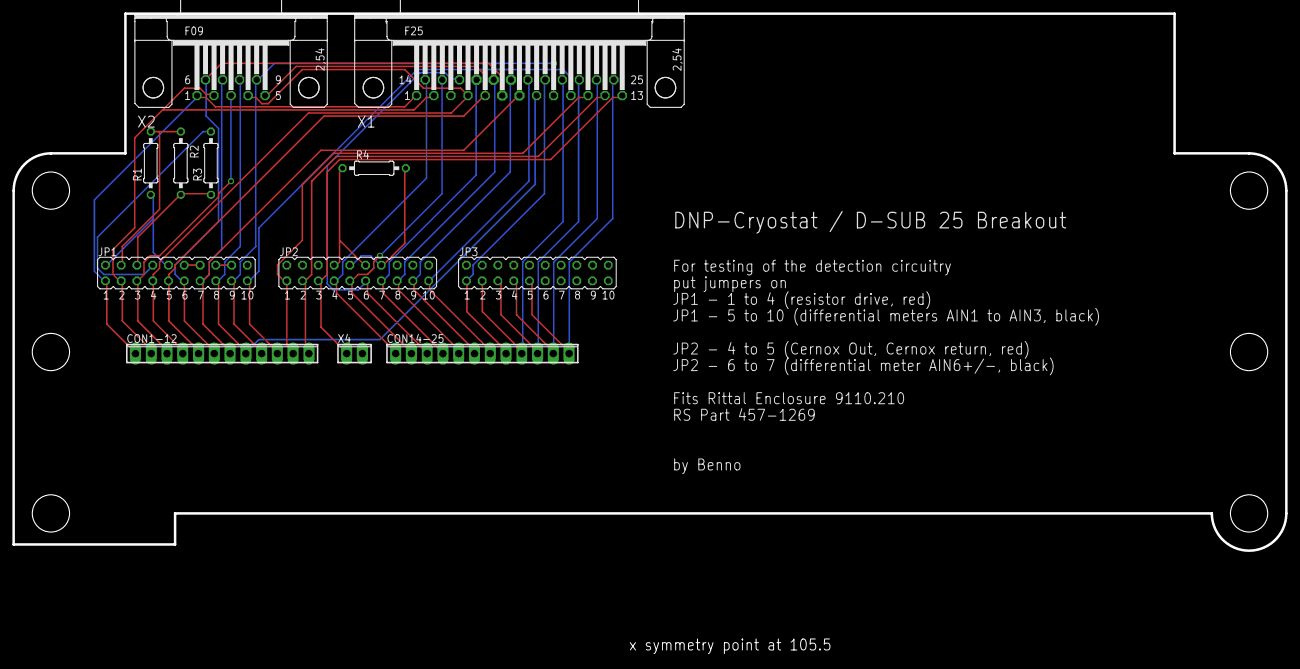
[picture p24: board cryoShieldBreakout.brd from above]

Board: 2 copper layers, 205.0 x 86.5 mm, 12 parts (0 on the bottom side), 33 nets.

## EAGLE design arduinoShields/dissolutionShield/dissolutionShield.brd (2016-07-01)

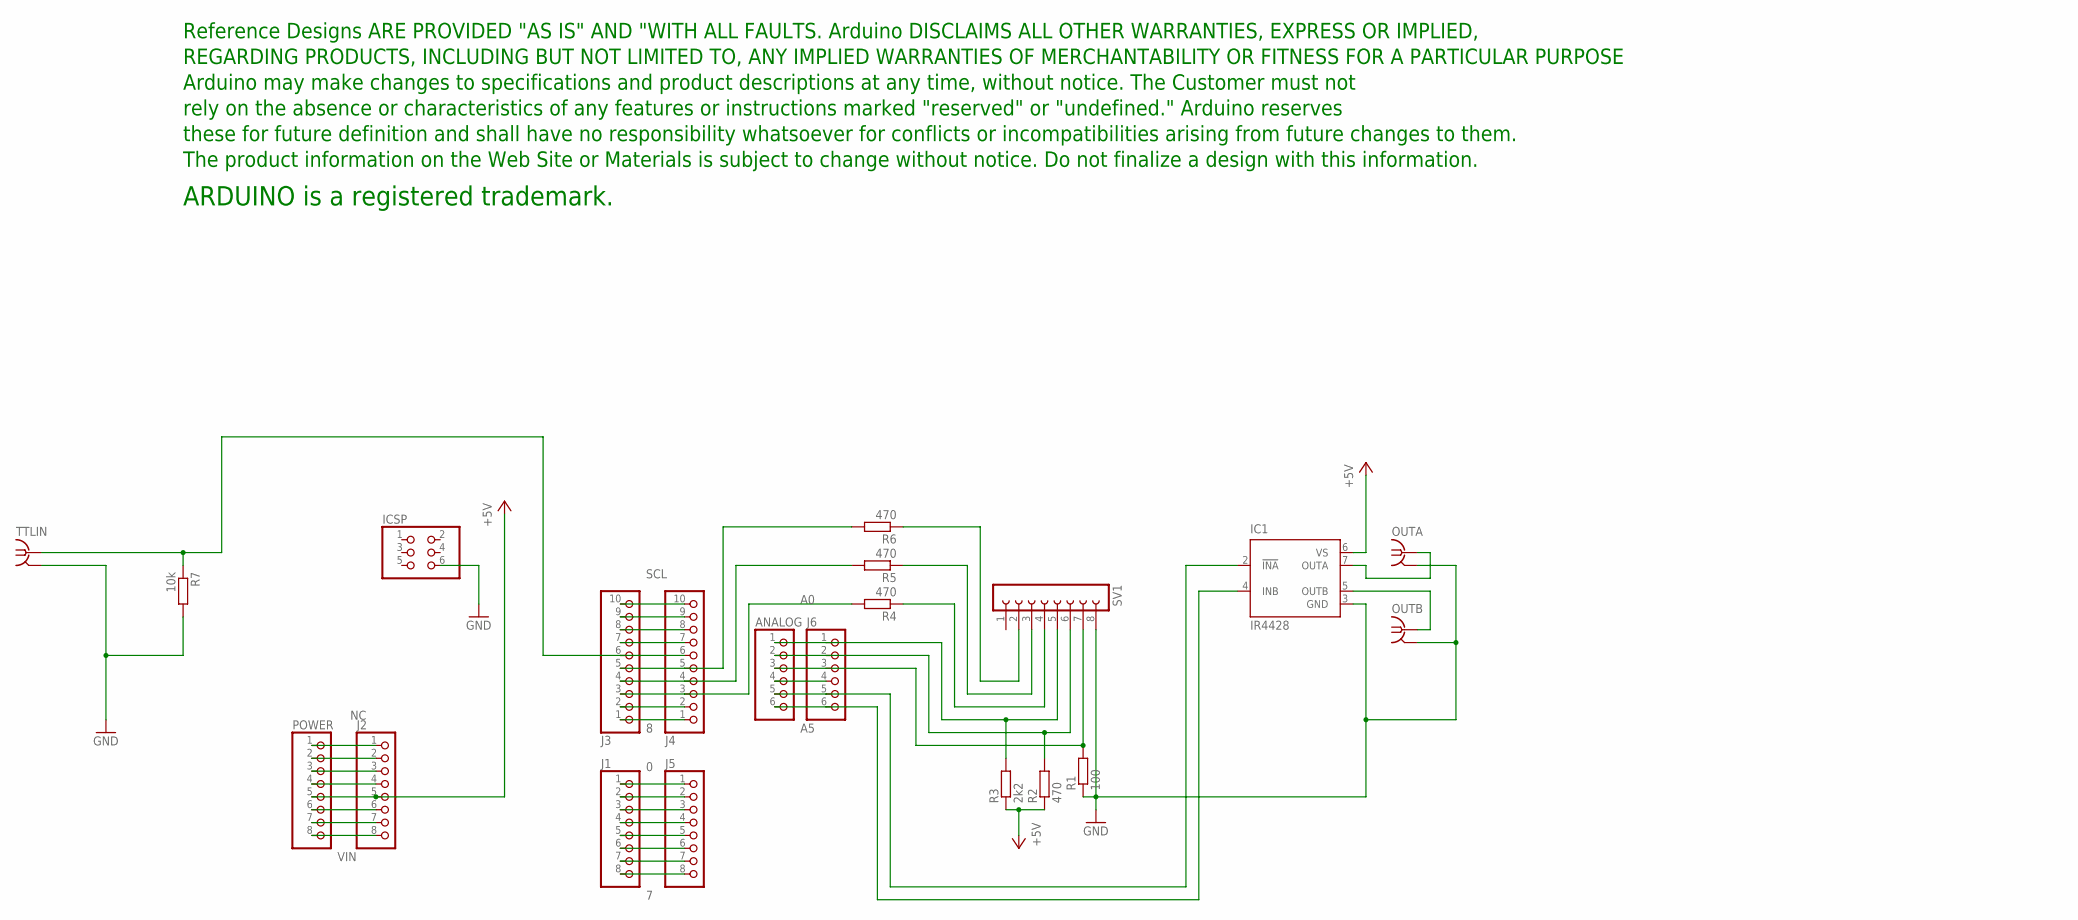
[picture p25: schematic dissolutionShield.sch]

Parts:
ANALOG: PINHD-1X6; 1X06
IC1: IR4428; DIL08
ICSP: PINHD-2X3; 2X03
J1, J2, J5: PINHD-1X8TH; 1X08-TH
J3, J4: PINHD-1X10TH; 1X10-TH
J6: PINHD-1X6; 1X06
OUTA: BU-SMA-H
OUTB: BU-SMA-H
POWER: PINHD-1X8TH; 1X08-TH
R1: 100; 0207/10
R2, R4, R5, R6: 470; 0207/10
R3: 2k2; 0207/10
R7: 10k; 0207/10
SV1: FE08-1; FE08
TTLIN: BU-SMA-H
U$1: DISCLAIMER

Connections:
0: J1.1, J5.1
1: J1.2, J5.2
2: J1.3, J5.3
3: J1.4, J5.4
4: J1.5, J5.5
5: J1.6, J5.6
6: J1.7, J5.7
7: J1.8, J5.8
8: J3.1, J4.1
9: J3.2, J4.2
10: J3.3, J4.3, R4.2
11: J3.4, J4.4, R5.2
+3V3: J2.4, POWER.4
+5V: IC1.6 (VS), J2.5, POWER.5, R2.1, R3.1
A0: ANALOG.1, J6.1, R3.2, SV1.5
A1: ANALOG.2, J6.2, R2.2, SV1.6
A2: ANALOG.3, J6.3, R1.2, SV1.7
A3: ANALOG.4, J6.4
A4: ANALOG.5, IC1.2 (!INA), J6.5
A5: ANALOG.6, IC1.4 (INB), J6.6
AREF: J3.8, J4.8
GND: IC1.3 (GND), ICSP.6, J2.6, J2.7, J3.7, J4.7, OUTA.2, OUTA.3 (2), OUTA.4 (2), OUTA.5 (2), OUTB.2, OUTB.3 (2), OUTB.4 (2), OUTB.5 (2), POWER.6, POWER.7, R1.1, R7.2, SV1.8, TTLIN.2, TTLIN.3 (2), TTLIN.4 (2), TTLIN.5 (2)
IOREF: J2.2, POWER.2
N12: J3.5, J4.5, R6.2
N13: J3.6, J4.6, R7.1, TTLIN.1
unnamed: IC1.7 (OUTA), OUTA.1
unnamed: IC1.5 (OUTB), OUTB.1
unnamed: R4.1, SV1.4
unnamed: R5.1, SV1.3
unnamed: R6.1, SV1.2
NC: J2.1, POWER.1
RESET: J2.3, POWER.3
SCL: J3.10, J4.10
SDA: J3.9, J4.9
VIN: J2.8, POWER.8

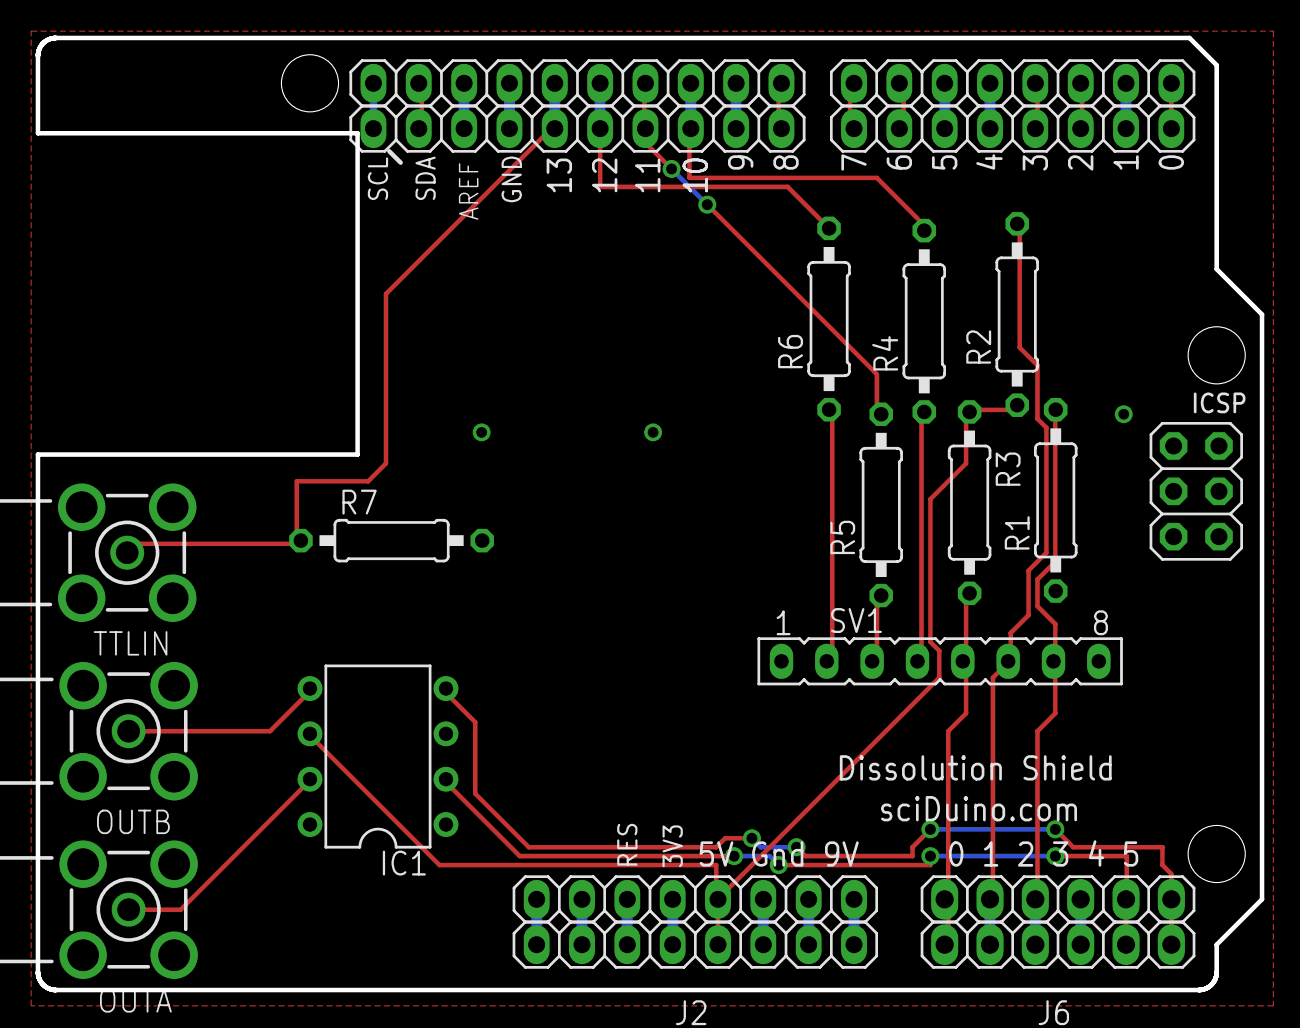
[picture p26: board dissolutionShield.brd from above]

Board: 2 copper layers, 68.6 x 53.3 mm, 22 parts (0 on the bottom side), 35 nets.

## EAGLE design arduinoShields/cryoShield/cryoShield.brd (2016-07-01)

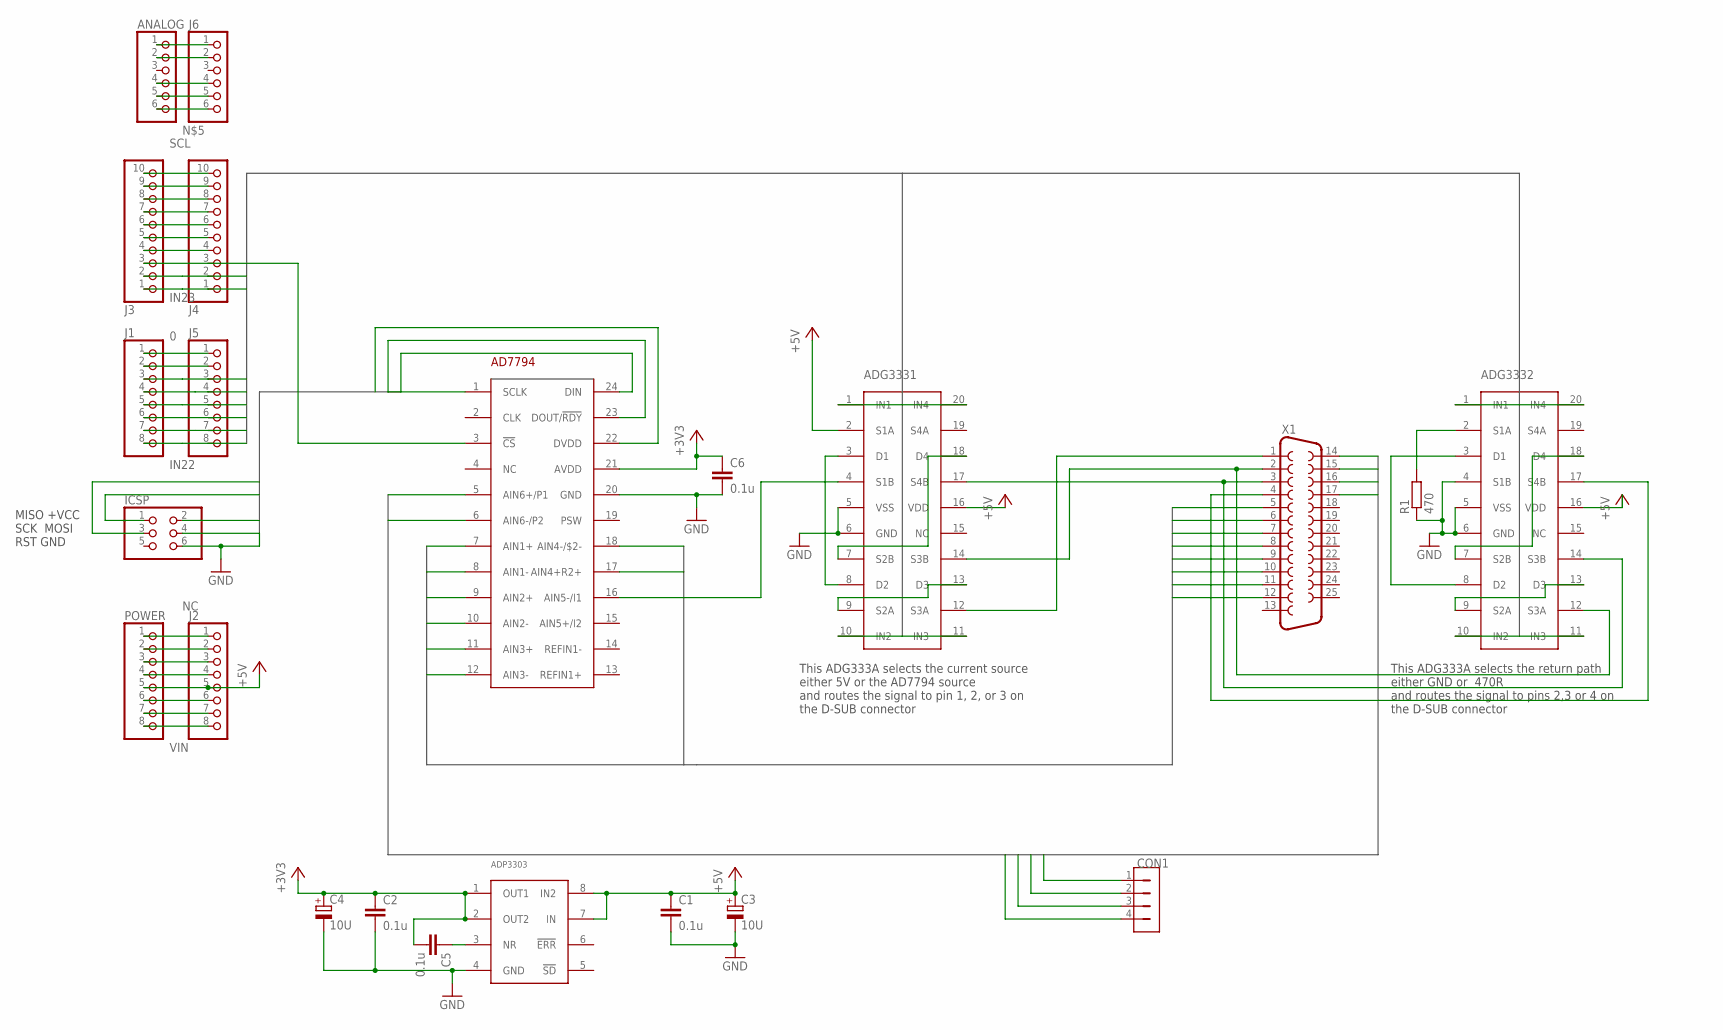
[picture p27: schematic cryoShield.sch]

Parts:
AD7794: AD7794; TSSOP24
ADG3331, ADG3332: ADG333; SOIC20S
ADP3303: ADP3303; SOIC8
ANALOG: PINHD-1X6; 1X06
C1, C2, C5, C6: 0.1u; C0805
C3, C4: 10U; CPOL1206
CON1: MICROCLASP4
ICSP: PINHD-2X3; 2X03
J1, J2, J5: PINHD-1X8TH; 1X08-TH
J3, J4: PINHD-1X10TH; 1X10-TH
J6: PINHD-1X6; 1X06
POWER: PINHD-1X8TH; 1X08-TH
R1: 470; 0207/10
X1: F25H

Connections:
0: J1.1, J5.1
1: J1.2, J5.2
+3V3: AD7794.21 (AVDD), ADP3303.1 (OUT1), ADP3303.2 (OUT2), C2.1, C4.1 (+), C5.2, C6.1, J2.4, POWER.4
+5V: ADG3331.2 (S1A), ADG3331.16 (VDD), ADG3332.16 (VDD), ADP3303.7 (IN), ADP3303.8 (IN2), C1.1, C3.1 (+), J2.5, POWER.5
A0: ANALOG.1, J6.1
A1: ANALOG.2, J6.2
A3: ANALOG.4, J6.4
ADG3332: ADG3332.7 (S2B), ADG3332.18 (D4)
AIN1+: AD7794.7 (AIN1+), X1.5
AIN1-: AD7794.8 (AIN1-), X1.6
AIN2+: AD7794.9 (AIN2+), X1.7
AIN2-: AD7794.10 (AIN2-), X1.8
AIN3+: AD7794.11 (AIN3+), X1.9
AIN3-: AD7794.12 (AIN3-), X1.10
AIN4+: AD7794.17 (AIN4+R2+), X1.11
AIN4-: AD7794.18 (AIN4-/$2-), X1.12
AIN6+: AD7794.5 (AIN6+/P1), CON1.3, X1.16
AIN6-: AD7794.6 (AIN6-/P2), CON1.4, X1.17
CERNOXHIGH: CON1.1, X1.14
CERNOXLOW: CON1.2, X1.15
GND: AD7794.20 (GND), ADG3331.5 (VSS), ADG3331.6 (GND), ADG3332.4 (S1B), ADG3332.5 (VSS), ADG3332.6 (GND), ADP3303.4 (GND), C1.2, C2.2, C3.2 (-), C4.2 (-), C6.2, ICSP.6, J2.6, J2.7, J3.7, J4.7, POWER.6, POWER.7, R1.1
IN11: ADG3331.1 (IN1), J1.3, J5.3
IN12: ADG3331.10 (IN2), J1.4, J5.4
IN13: ADG3331.11 (IN3), J1.5, J5.5
IN14: ADG3331.20 (IN4), J1.6, J5.6
IN21: ADG3332.1 (IN1), J1.7, J5.7
IN22: ADG3332.10 (IN2), J1.8, J5.8
IN23: ADG3332.11 (IN3), J3.1, J4.1
IN24: ADG3332.20 (IN4), J3.2, J4.2
IOREF: J2.2, POWER.2
MISO: AD7794.23 (DOUT/!RDY), ICSP.1
MOSI: AD7794.24 (DIN), ICSP.4
unnamed: ADG3331.14 (S3B), ADG3332.12 (S3A), X1.2
unnamed: ADG3331.3 (D1), ADG3331.8 (D2)
unnamed: ANALOG.5, J6.5
unnamed: ANALOG.6, J6.6
unnamed: ADG3331.9 (S2A), ADG3331.13 (D3)
unnamed: ADG3331.7 (S2B), ADG3331.18 (D4)
unnamed: ADG3331.12 (S3A), X1.1
unnamed: ADG3331.17 (S4B), ADG3332.14 (S3B), X1.3
unnamed: ADG3332.2 (S1A), R1.2
unnamed: ADG3332.3 (D1), ADG3332.8 (D2)
unnamed: ADG3332.9 (S2A), ADG3332.13 (D3)
unnamed: AD7794.16 (AIN5-/I1), ADG3331.4 (S1B)
unnamed: ADP3303.3 (NR), C5.1
unnamed: ADG3332.17 (S4B), X1.4
unnamed: AD7794.3 (!CS), J3.3, J4.3
unnamed: J3.4, J4.4
unnamed: J3.5, J4.5
unnamed: J3.6, J4.6
unnamed: J3.8, J4.8
NC: J2.1, POWER.1
RESET: J2.3, POWER.3
SCK: AD7794.1 (SCLK), ICSP.3
SCL: J3.10, J4.10
SDA: J3.9, J4.9
VCC: AD7794.22 (DVDD), ICSP.2
VIN: J2.8, POWER.8

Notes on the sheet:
This ADG333A selects the current source either 5V or the AD7794 source and routes the signal to pin 1, 2, or 3 on the D-SUB connector
This ADG333A selects the return path either GND or 470R and routes the signal to pins 2,3 or 4 on the D-SUB connector
MISO +VCC SCK MOSI RST GND

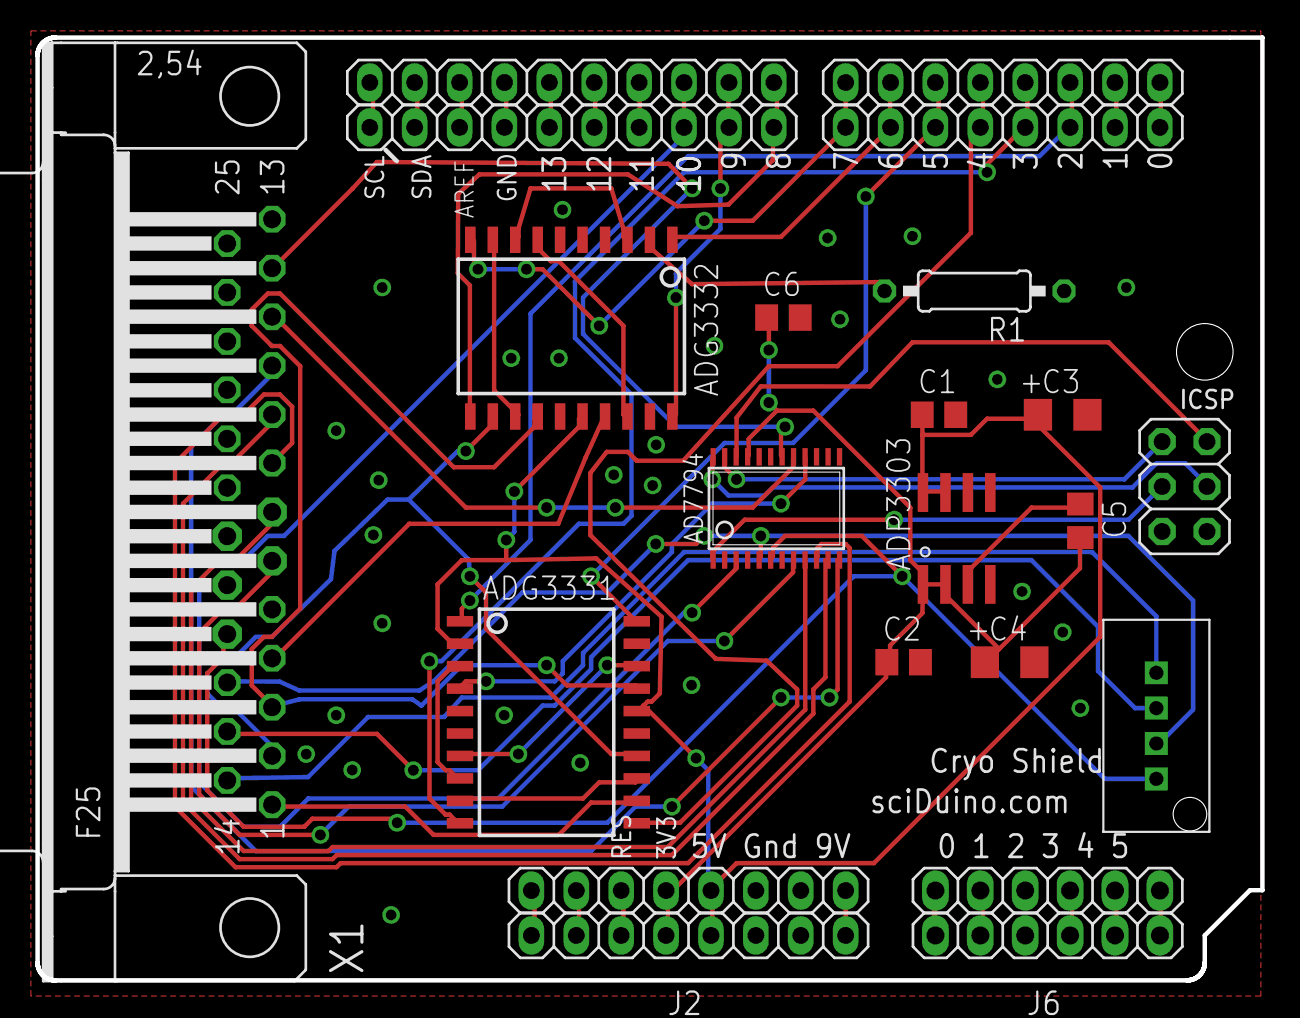
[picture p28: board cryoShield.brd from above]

Board: 2 copper layers, 69.3 x 53.3 mm, 22 parts (0 on the bottom side), 58 nets.

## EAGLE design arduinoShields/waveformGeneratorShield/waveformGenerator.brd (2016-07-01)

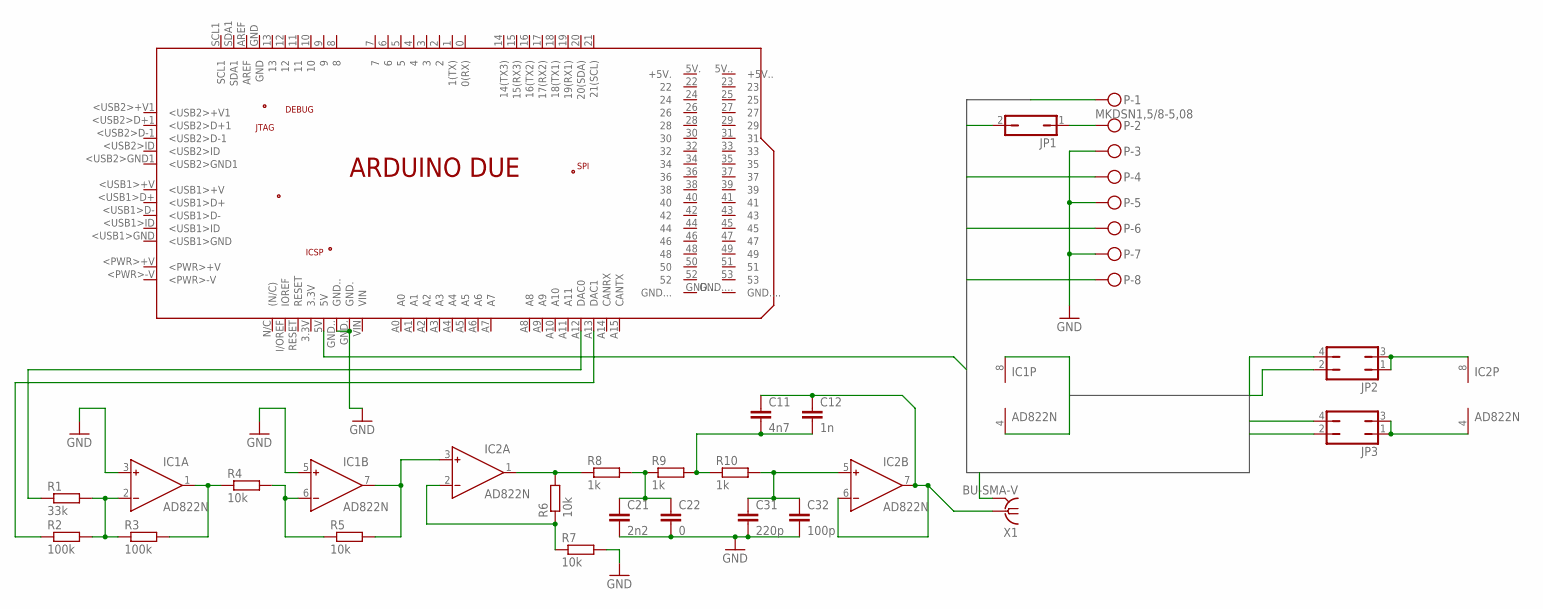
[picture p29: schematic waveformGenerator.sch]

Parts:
C11: 4n7; C050-030X075
C12: 1n; C050-030X075
C21: 2n2; C050-030X075
C22: 0; C050-030X075
C31: 220p; C050-030X075
C32: 100p; C050-030X075
IC1, IC2: AD822N; DIL08
JP1: JP1Q; JP1
JP2, JP3: JP2Q
P: MKDSN1,5/8-5,08
PCB1: ARDUINO_DUE
R1: 33k; 0207/10
R2, R3: 100k; 0207/10
R4, R5, R6, R7: 10k; 0207/10
R8, R9, R10: 1k; 0207/10
X1: BU-SMA-V

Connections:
+5: JP1.2, PCB1.5V
+15: IC1.8 (V+), JP2.2, P.8
+24: JP2.4, P.4
-15: IC1.4 (V-), JP3.2, P.6
GND: C21.2, C22.2, C31.2, C32.2, IC1.3 (IN+), IC1.5 (IN+), JP3.4, P.1, P.3, P.5, P.7, PCB1.GND., PCB1.GND.., R7.2, X1.2, X1.3 (2), X1.4 (2), X1.5 (2)
unnamed: PCB1.A12 (DAC0), R1.1
unnamed: PCB1.A13 (DAC1), R2.1
unnamed: IC1.2 (IN-), R1.2, R2.2, R3.1
unnamed: JP1.1, P.2
unnamed: IC1.1 (OUT), R3.2, R4.1
unnamed: IC1.6 (IN-), R4.2, R5.1
unnamed: IC1.7 (OUT), IC2.3 (IN+), R5.2
unnamed: IC2.4 (V-), JP3.1, JP3.3
unnamed: IC2.8 (V+), JP2.1, JP2.3
unnamed: C11.1, C12.1, IC2.6 (IN-), IC2.7 (OUT), X1.1
unnamed: IC2.2 (IN-), R6.1, R7.1
unnamed: IC2.1 (OUT), R6.2, R8.1
unnamed: C21.1, C22.1, R8.2, R9.1
unnamed: C11.2, C12.2, R9.2, R10.1
unnamed: C31.1, C32.1, IC2.5 (IN+), R10.2

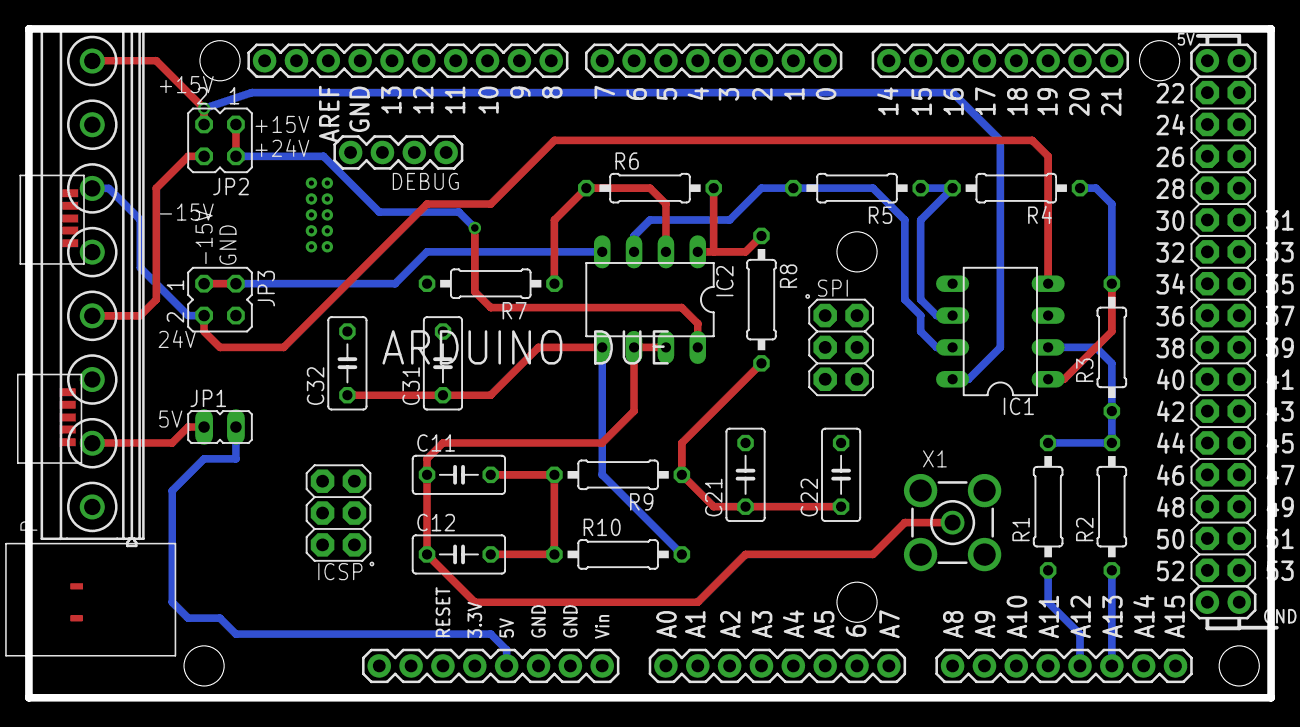
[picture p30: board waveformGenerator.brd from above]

Board: 2 copper layers, 99.1 x 53.3 mm, 24 parts (0 on the bottom side), 20 nets.

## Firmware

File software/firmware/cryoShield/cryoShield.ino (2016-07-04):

#include <Wire.h>
#include <LiquidCrystal_I2C.h>
#include <Ethernet.h> //Load Ethernet Library
#include <EthernetUdp.h> //Load the Udp Library
//- See more at: http://www.toptechboy.com/#sthash.A8STFLcE.dpuf
#include <SPI.h>
#include "ad7794.h"


//Ethernet Stuff 
byte mac[] ={ 0x90, 0xA2, 0xDA, 0x0E, 0xAD, 0x0A  }; //Assign mac address
IPAddress ip(10, 1, 15, 243); //Assign the IP Adress
unsigned int localPort = 5000; // Assign a port to talk over
char packetBuffer[UDP_TX_PACKET_MAX_SIZE]; //dimensian a char array to hold our data packet
String datReq; //String for our data
int packetSize; //Size of the packet
EthernetUDP Udp; // Create a UDP Object

/* THIS EXAMPLE IS WORKING AS OF FRI, MARCH 21 2014, BEFORE I LEFT FOR AMERICA.
THE IMPORTANT BIT IS NEVER TO SWITCH ON BIAS


The instrumentation amplifier needs headroom, so it will only work well if the lower voltage is high enough above ground.
To solve this problem by switching on bias (which should bias V- to Vdd/2) never worked for me.
Maybe the chip cannot source enough current, but I think I have checked that as well.

TASKS:
- restructure the ad7794 library according to the various registers.


//This example has the lcb bit removed, but introduces interrupts
*/

ad7794 ad(12);
long int dataBuffer[1024];

//ad7794 ad(9);

int lightOn = 1;
int millisStart = 0;
int duration = 0;
float range;
char command;
int voltageInt = 0;
float voltageVolt = 0.0;
int resistor;
int biasGenerator;//this governs the AD7794 bias generator. 0: off
int gain = 32;
int gainAB = 32;
int gainCERNOX = 128;
int dataLength = 100;
float dwellTime = 10;
int channel;
String rString = "";
int current = 10;//current in uA

boolean BIAS;
boolean DEBUG = true;

long val = 0;

// DIGITAL PINS - V2
#define S11 2
#define S12 3
#define S13 5
#define S14 6
#define S21 7
#define S22 8
#define S23 9
#define S24 11
#define AD7794CS 12 //note that this causes trouble on the UNO
//cf. https://www.circuitsathome.com/mcu/running-multiple-slave-devices-on-arduino-spi-bus

// I2C LCD DISPLAY STUFF
//#include <LCD.h>
//#include <LiquidCrystal_I2C.h>  // F Malpartida's NewLiquidCrystal library

#define I2C_ADDR    0x27  // Define I2C Address for controller
#define BACKLIGHT_PIN  3
#define En_pin  2
#define Rw_pin  1
#define Rs_pin  0
#define D4_pin  4
#define D5_pin  5
#define D6_pin  6
#define D7_pin  7

#define  LED_OFF  0
#define  LED_ON  1
LiquidCrystal_I2C  lcd(I2C_ADDR,En_pin,Rw_pin,Rs_pin,D4_pin,D5_pin,D6_pin,D7_pin);


void setup() {
  //define output ad7794
  pinMode(12, OUTPUT);


  lcd.begin (16,2);  // initialize the lcd
  //Switch on the backlight
  lcd.setBacklightPin(BACKLIGHT_PIN,POSITIVE);
  lcd.setBacklight(LED_OFF);
  lcd.backlight();
  
  lcd.print("Starting up");
  
  //pinMode(10, INPUT_PULLUP);
  Serial.begin(57600);
  SPI.begin();
  
  Ethernet.begin( mac, ip); //Inialize the Ethernet
  Udp.begin(localPort); //Initialize Udp

  ad.reset();
  Serial.print("Status: ");
  Serial.println(ad.getStatus(), BIN);

  ///////////////////////////////////////////////////////////////////////////
  ///////////// CONFIGURATION REGISTER //////////////////////////////////////
  ///////////////////////////////////////////////////////////////////////////
  channel = 8;//set channel to 8 to monitor AVDD//4:   2.5 mV rather than 4mV
  biasGenerator = 0;//channel;
  
  //configurationRegister high
  //standard configuration: no bias, unipolar coding with boost and zero gain
  byte configHigh = B00011000;
  configHigh |= byte(int(log(gain)/log(2)));
  configHigh |= byte(biasGenerator) << 6;
  
  //configurationRegister low
  //standard configuration: Internal Reference, Buffered
  byte configLow = B10010000;
  configLow |= byte(channel-1); 
  
  if (DEBUG == true) {
    Serial.print("Configuration Register High: ");
    Serial.println(configHigh, BIN);

    Serial.print("Configuration Register Low: ");
    Serial.println(configLow, BIN);
  }
  
  ad.setConfigurationRegister(1, 8, 0);
  //ad.writeTwoRegisters(CONFIGURATION, configHigh, configLow);



  //curent source
  //0b11: 1mA
  //0b10: 210 uA
  //0b01: 10uA
  //0b00: off
  current = 10;
  ad.writeRegister(IOREG, 0b01);//
  delay(1);

  //mode: continuous conversion, 123 Hz
  ad.writeTwoRegisters(MODE, B00000000, B00000011);
  //ad.writeTwoRegisters(MODE, B00000000, B00001111);




  long conRegister = ad.readMultipleRegisters(CONFIGURATION, 2);
  byte ioRegister = ad.readRegister(IOREG);
  long modRegister = ad.readMultipleRegisters(MODE, 2);

  
  if (DEBUG == true) {
    Serial.print("Con: ");
    Serial.println(conRegister, BIN);

    Serial.print("IO: ");
    Serial.println(ioRegister, BIN);

    Serial.print("Mode: ");
    Serial.println(modRegister, BIN);
  }

  //attachInterrupt(10, readADC, FALLING);
  pinMode(2, OUTPUT);
  pinMode(3, OUTPUT);
  //pinMode(4, OUTPUT);
  pinMode(5, OUTPUT);
  pinMode(6, OUTPUT);
  pinMode(7, OUTPUT);
  pinMode(8, OUTPUT);
  pinMode(9, OUTPUT);
  pinMode(11, OUTPUT);
  


  // if AD7794 channel is 4, wire current through R1 (check the connection of AD1+ on the board.
  returnPath(channel, true);
  delay(1);
  drivePath(channel, false);
  delay(1);
}

void returnPath(int resistor, boolean BIAS) {
  if (BIAS == true) {
    digitalWrite(S21, HIGH);
  } else {
    digitalWrite(S21, LOW);
  }
  if (resistor == 1) {
    digitalWrite(S22, HIGH);
    digitalWrite(S23, HIGH);
    digitalWrite(S24, HIGH);
  } else if (resistor == 2) {
    digitalWrite(S22, HIGH);
    digitalWrite(S23, LOW);
    digitalWrite(S24, HIGH);
  } else if (resistor == 3) {
    digitalWrite(S22, LOW);
    digitalWrite(S24, LOW);
    digitalWrite(S23, HIGH);

  }
}

void drivePath(int resistor, boolean PLUSFIVE) {
  if (PLUSFIVE == true) {
    digitalWrite(S11, HIGH);
  } else {
    //note that in this case you may want to have the AD7794 current source programmed
    digitalWrite(S11, LOW);
  }
  if (resistor == 1) {
    digitalWrite(S12, HIGH);
    digitalWrite(S13, HIGH);
    digitalWrite(S14, HIGH);
  } else if (resistor == 2) {
    digitalWrite(S12, HIGH);
    digitalWrite(S13, LOW);
    digitalWrite(S14, HIGH);
  } else if (resistor == 3) {
    digitalWrite(S12, LOW);
    digitalWrite(S14, LOW);
    digitalWrite(S13, HIGH);
  }
}

void readADC() {
  //SET REGISTER 4 TO LOW IF ETHERNET SHIELD CONNECTED
  Serial.println("millis:" +  String(millis()));
  val = ad.readMultipleRegisters(DATA, 3);
  
  //Serial.println("Digitizer Level: " + String(float(val) / 0xffffff*100) + " %");
  //Serial.println("Voltage: " + String(float(val) / 0xffffff * 1.17/gain* 1000) + " mV");
  //Serial.println("Resistance: " + String(float(val) / 0xffffff * 1.17/gain/(current*1e-6)) + "Ohm");
}

void checkVCC() {
 ad.setConfigurationRegister(1, 8, 0);
 delay(100);
 val = ad.readMultipleRegisters(DATA, 3);
 Serial.println("Digitizer Level: " + String(float(val) / 0xffffff*100) + " %");
 Serial.println("Voltage: " + String(float(val) / 0xffffff * 1.17/8) + " V");

}

int probeCernox() {
  int start = millis();
  ad.setConfigurationRegister(gainCERNOX, 6, 0);
  delay(10);
  for (int c = 0; c < dataLength; c++) {
   //Serial.print(String(ad.readMultipleRegisters(DATA, 3)) + ","); 
   dataBuffer[c] = ad.readMultipleRegisters(DATA, 3);
   //dataBuffer[c] = ad.readMultipleRegisters(DATA, 3);
   //Serial.print(String(dataBuffer[c]) + ",");
   delay(dwellTime);
  }  
  Serial.println("Measuring Cernox takes " + String(millis() - start) + "ms");
  //dataToEthernet();
}

void dataToEthernet() {
  for (int c = 0; c < dataLength; c++) {
   //Serial.print(String(ad.readMultipleRegisters(DATA, 3)) + ","); 
   dataBuffer[c] = ad.readMultipleRegisters(DATA, 3);
   //dataBuffer[c] = ad.readMultipleRegisters(DATA, 3);
   delay(1);
  }  
}

void dataToSerial() {
 for (int c = 0; c < dataLength; c++) {
  Serial.print(dataBuffer[c], HEX);
  Serial.print(",");
 } 
 Serial.print("\n");
}

void probeVDD() {
  Serial.println("PROBING VDD \n=====================");
  ad.setConfigurationRegister(1, 8, 0); 
  delay(500);
  val = ad.readMultipleRegisters(DATA, 3);
  Serial.println("Val: " +  String(val, HEX));
  Serial.println("Digitizer Level: " + String(float(val) / 0xffffff*100) + " %");
  Serial.println("Voltage: " + String(float(val) / 0xffffff * 1.17*6) + " V");
}

void reportRegistersToSerial() {
 Serial.println("Register\t Value\n=======================");
 delay(3);
 Serial.println("Mode\t\t" + String(ad.readMultipleRegisters(MODE, 2), BIN));
 delay(3);
 Serial.println("Configuration\t" +   String(ad.readMultipleRegisters(CONFIGURATION, 2), BIN)); 
 delay(3);
 Serial.println("IOREG\t" +   String(ad.readRegister(IOREG), BIN)); 
}

int probeAllenBradley(int channel) {
  //configure channel
  ad.setConfigurationRegister(32, channel, 0);

  ad.writeRegister(IOREG, 0b01);

  
  returnPath(channel, false);
  drivePath(channel, true);
  delay(1000);
  returnPath(channel, true);
  drivePath(channel, false);
  delay(1);

  delay(10);
  
  int startTime = millis();
  for (int c = 0; c < dataLength; c++) {
   //Serial.print(String(ad.readMultipleRegisters(DATA, 3)) + ",");
  boolean dataNotRead = true;
   int count = 0;
   while (dataNotRead) {
     count++;
     byte currentStatus = ad.getStatus();
    if (currentStatus < 100) {
     dataBuffer[c] = ad.readMultipleRegisters(DATA, 3);
     dataNotRead = false;
    } else {
     delay(1);
     if (count > 10) {
      Serial.println("10 attempts");
     }
   } 
   }
   delay(dwellTime);
  }  
  //switch off current source
  ad.writeRegister(IOREG, 0b00);
 // for (int c = 0; c < 256; c++) {
 //     Serial.print(String(dataBuffer[c])+ ","); 
 // }
  
  int stopTime = millis();
  Serial.println("Total time: " + String(stopTime-startTime));

  Serial.print("\nMeasured channel "+ String(channel)); 
  return dataBuffer[1023];
}
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

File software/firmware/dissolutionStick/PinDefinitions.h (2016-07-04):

#define I2C_ADDR    0x27  // Define I2C Address for controller
#define BACKLIGHT_PIN  3
#define En_pin  2
#define Rw_pin  1
#define Rs_pin  0
#define D4_pin  4
#define D5_pin  5
#define D6_pin  6
#define D7_pin  7

#define  LED_OFF  0
#define  LED_ON  1

// other pins: 20 ground, 21 + 3.3V
const int valve1 = 2;//He gas open
const int valve2 = 3;//He gas close (optional)
const int valve3 = 4;
const int valve4 = 5;//valve on dissolution stick 
const int valve5 = 6;
const int valve6 = 7;//KF50 Sample Space
const int valve7 = 8;
const int valve8 = 9;//He inlet sample space Fast

const int trigger = 13;

const int ledButton = 10; //pushButton
const int ledRed = 11; //red
const int ledGreen = 12; //green

const int pushButton = 0;

const int ttlIN = 13;
const int ttlOUTB = A4;
const int ttlOUTA = A5;

const int transformer1 = 50;
const int transformer2 = 51;

class PinDefinitions {
  public:
    PinDefinitions();
    void configurePins();
};

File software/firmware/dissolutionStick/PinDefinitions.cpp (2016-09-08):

/* the only use of this class is to configure all the necessary pins as output pins */
#include "Arduino.h"
#include "PinDefinitions.h"

PinDefinitions::PinDefinitions() {
}

void PinDefinitions::configurePins() {
  //for some reason this stuff needs to be called separately  
 Serial.println("Now we define the pins");
   
  pinMode(ledRed, OUTPUT);
  pinMode(ledGreen, OUTPUT);
  pinMode(ledButton, OUTPUT);  
  //attachInterrupt(pushButton, dissolve, RISING);
  
  pinMode(valve1, OUTPUT);
  digitalWrite(valve1, HIGH);

  pinMode(valve2, OUTPUT);
  digitalWrite(valve2, LOW);
  
  pinMode(valve3, OUTPUT);
  digitalWrite(valve3, LOW);

  pinMode(valve4, OUTPUT);
  digitalWrite(valve4, LOW);
 
  pinMode(valve5, OUTPUT);
  digitalWrite(valve5, LOW);
  
  pinMode(valve6, OUTPUT);
  digitalWrite(valve6, LOW);
  
  pinMode(valve7, OUTPUT);
  digitalWrite(valve7, LOW);
  
  pinMode(valve8, OUTPUT);
  digitalWrite(valve8, LOW);


  pinMode(trigger, OUTPUT);
  digitalWrite(trigger, LOW);

  pinMode(transformer1, OUTPUT);
  pinMode(transformer2, OUTPUT);
  digitalWrite(transformer1, LOW);
  digitalWrite(transformer2, LOW);

  pinMode(ttlOUTA, OUTPUT);
  pinMode(ttlOUTB, OUTPUT);
  pinMode(ttlIN, INPUT);
  
  pinMode(20, OUTPUT);
  pinMode(21, OUTPUT);
  digitalWrite(20, LOW);
  digitalWrite(21, HIGH);
  
  digitalWrite(ledButton, HIGH);
  digitalWrite(ledRed, HIGH);
  digitalWrite(ledGreen, LOW);


}

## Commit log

2016-07-01 Initial commit for GitHub.
    [CAHB-10-B2A-050-AAAAPA-000.SLDASM, CAHB-10-B2A-050-AAAAPA-000.x_b, HallProbeClampOxInst.SLDPRT, HallProbeClampOxInst.STL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]
2016-09-11 Add simple temperatureMonitor script for Mercury Temperature Controller
2016-12-10 Minor software changes, add drawings
    [capacitorOuterPart.SLDPRT]
2016-12-10 Restructure dnpInsert folder
    [cavity.SLDDRW, cavity.SLDPRT, cavityLid.SLDDRW, cavityLid.SLDPRT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]
